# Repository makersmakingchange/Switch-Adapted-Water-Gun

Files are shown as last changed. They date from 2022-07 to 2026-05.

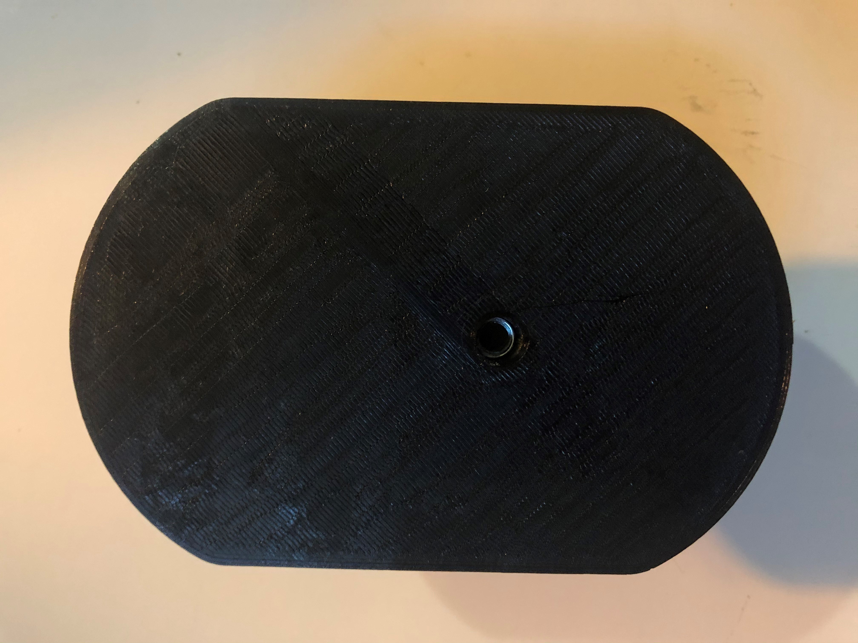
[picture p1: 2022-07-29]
Photos/Step 23.jpg

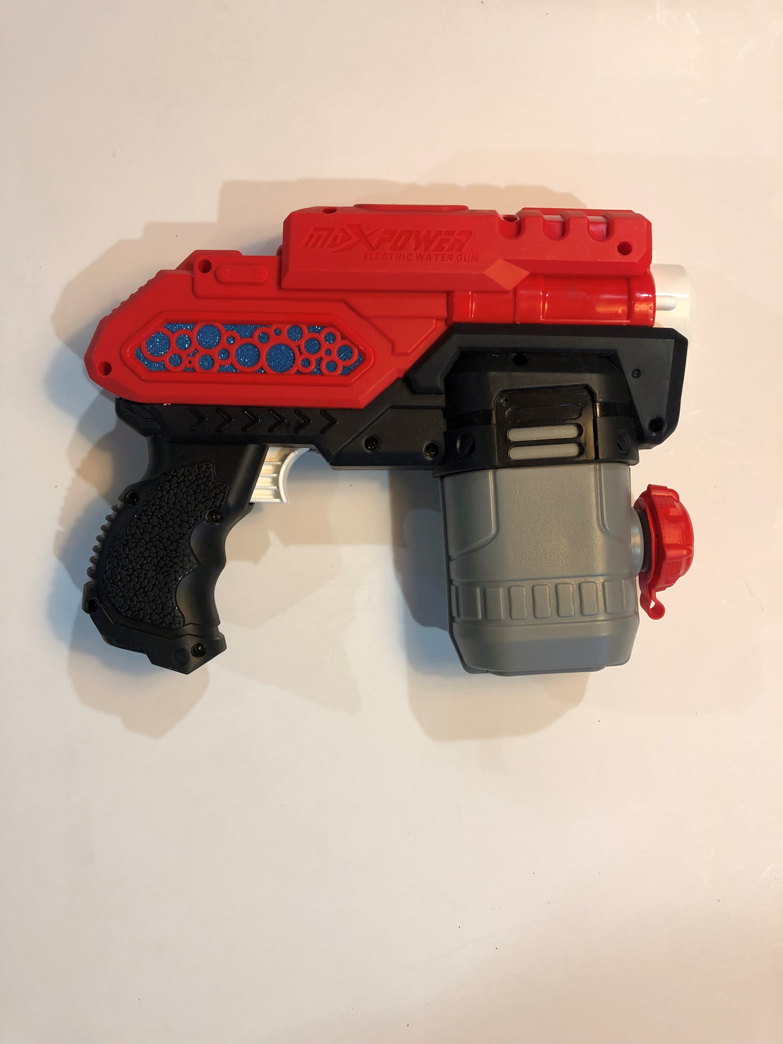
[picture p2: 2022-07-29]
Photos/Step 1.jpg

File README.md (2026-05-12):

# Switch Adapted Water Gun

> [!IMPORTANT]
2026-May-12 Unfortunately, the commercial water gun that this design and adaptation method was based on is no longer available for purchase (https://www.amazon.ca/HITNEXT-Electric-Children-Operated-Automatic/dp/B0919VSGYH). 
>

An adapted water gun that uses a 3.5 mm assistive switch.



## More info at
- [Makers Making Change Project Page](https://makersmakingchange.com/project/switch-adapted-water-gun/)

## Getting Started
#### 1. How to build this device

All of the files and instructions required to adapted the bubble blower are contained within this repository. Refer to the Maker Checklist below.

#### 2. How to request a build of this device

If you would like to obtain a switch adapted bubble blower but do not have the skills or equipment to do so, you may submit a build request through the [MMC Library Page](  https://makersmakingchange.com/project/switch-adapted-water-gun/). The requestor is responsible for the cost of materials and any shipping.

#### 3. How to build this device for someone else

If you have the skills and equipment to build this device, and would like to donate your time to create the switch for someone who needs it, visit the [MMC Maker Wanted](https://makersmakingchange.com/maker-wanted/) section.

## Files
### Documentation
| Document              | Version | Link |
|-----------------------|---------|------|
| Assembly Guide        | 1.0     | [Switch Adapted Water Gun Assembly Guide](/Documentation/Switch_Adapted_Water_Gun_Assembly_Guide_v1.0.pdf)|
| Design Rationale      | 1.0     | [Switch Adapted Water Gun Design Rationale](/Documentation/Switch_Adapted_Water_Gun_Design_Rationale_v1.0.pdf)|
| Bill of Materials     | 1.0     | [Switch Adapted Water Gun Bill of Materials](/Documentation/Working_Documents/Switch_Adapted_Water_Gun_BOM.xlsx)|
| Maker Checklist       | 1.0     | [Switch Adapted Water Gun Maker Checklist](/Documentation/Switch_Adapted_Water_Gun_Maker_Checklist_v1.0.pdf)|
| User Guide            | 1.0     | [Switch Adapted Water Gun User Guide](/Documentation/Switch_Adapted_Water_Gun_User_Guide_v1.0.pdf)|
| Changelog             | 1.0     | [Switch Adapted Water Gun Changelog](/Documentation/Switch_Adapted_Water_Gun_Changelog_v1.0.pdf)|

## Attribution
Toy adaption by Kerilyn Kennedy – Makers Making Change

3D Printed Water Gun Stand designed by Kerilyn Kennedy – Makers Making Change

Documentation by Neil Squire / Makers Making Change

## License
<br /><span xmlns:dct="http://purl.org/dc/terms/" property="dct:title">Switch Adapted Water Gun</span> by <a xmlns:cc="http://creativecommons.org/ns#" href="www.makersmakingchange.com" property="cc:attributionName" rel="cc:attributionURL">Neil Squire</a> is licensed under a <a rel="license" href="http://creativecommons.org/licenses/by-sa/4.0/">Creative Commons Attribution-ShareAlike 4.0 International License</a>.

----

<!-- ABOUT MMC START -->
## About Makers Making Change
[Makers Making Change Logo](https://www.makersmakingchange.com/)

Makers Making Change is a program of [Neil Squire](https://www.neilsquire.ca/), a Canadian non-profit that uses technology, knowledge, and passion to empower people with disabilities.

Makers Making Change leverages the capacity of community based Makers, Disability Professionals and Volunteers to develop and deliver affordable Open Source Assistive Technologies.

 - Website: [www.MakersMakingChange.com](https://www.makersmakingchange.com/)
 - GitHub: [makersmakingchange](https://github.com/makersmakingchange)
 - Bluesky: [@makersmakingchange.bsky.social](https://bsky.app/profile/makersmakingchange.bsky.social)
 - Instagram: [@makersmakingchange](https://www.instagram.com/makersmakingchange)
 - Facebook: [makersmakechange](https://www.facebook.com/makersmakechange)
 - LinkedIn: [Neil Squire Society](https://www.linkedin.com/company/neil-squire-society/)
 - Thingiverse: [makersmakingchange](https://www.thingiverse.com/makersmakingchange/about)
 - Printables: [MakersMakingChange](https://www.printables.com/@MakersMakingChange)

### Contact Us
For technical questions, to get involved, or to share your experience we encourage you to [visit our website](https://www.makersmakingchange.com/) or [contact us](https://www.makersmakingchange.com/s/contact).
<!-- ABOUT MMC END -->

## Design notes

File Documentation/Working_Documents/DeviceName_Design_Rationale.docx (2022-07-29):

# Introduction

We were brought the idea of adding a switch adapted water gun to the MMC library by the IWK. People with limited hand function might not be able to hold a water gun or do the pumping required to operate most water guns. They also might have difficulty pulling the trigger on a water gun as they often require a medium-high activation force. The Switch Adapted Water Gun can be used with just the push of a 3.5mm switch.

# Research

## Commercial Alternatives:

Water Gun with Lights Switch Adapted - $58.10

Switch-adapted Water Gun Soaker (https://www.seemethrive.org/product-page/switch-adapted-water-gun-soaker) - $45.00

## DIY Alternatives:

Adaptions 4 Kidz: Switch Adapted Water Gun Fun (http://adaptions4kidz.blogspot.com/2012/07/switch-adapted-water-gun-fun.html)

# Requirements

## Goals

G01 | Switch adapt the water gun
G02 | Design a 3D printed stand for the water gun
G03

## Functional Requirements

F01 | That the water gun can be adapted to work with a 3.5mm switch.
F02
F03

## Non-functional Requirement

NF01 | That the adaption is easy enough so other volunteer makers can do it themselves.
NF02
NF03

## Constraints

C01
C02
C03

# Ideation

The water gun planned to be used in this project is shown below. It is a battery-operated water gun that requires no pumping to squirt water. It was purchased from Amazon (https://www.amazon.ca/Electric-Battery-Operated-Swimming-Fighting/dp/B08S79325P?rnid=12035759011&s=toys). The idea is to add a jack in parallel with the existing switch in the water gun.

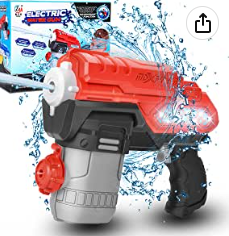
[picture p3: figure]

# Conceptual Design

## Concept 1 – Adding the Assistive Switch in Parallel

The original concept for the water gun adaptation was to be able to add an assistive switch in parallel with the existing switch. This allows for either the original trigger or the assistive switch to work to operate the toy. However, upon further investigation it was determined that it was quite difficult to get access to the original switch. As shown below, a drill was used to cut through the plastic to get access to the switch wires. Once a few holes were drilled, flush cutters were used to snap the reminder of the plastic away. Even with this new opening, I was still not able to access the original switch to solder in parallel. If one wanted the switch in parallel, it could be done by cutting into the yellow and blue wires and soldering in the assistive switch. Note, there is not much room to work with as wires a small and there is not much slack to work with. It can be done but it is not recommended to do it this way for a group build as it was time consuming to drill into this piece and there is a risk of damaging the wires when drilling through.

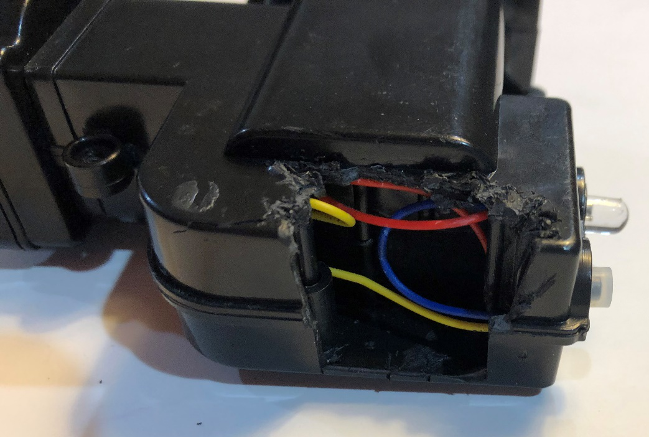
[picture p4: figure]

## Concept 2 – Adding the Assistive Switch in Series

The next route taken was to add the assistive switch in series with the original switch. This means that the original switch would have to be held in the “on” position all the time in order for the assistive switch to work. This would most easily be done with a battery interrupter.

# Detailed Design

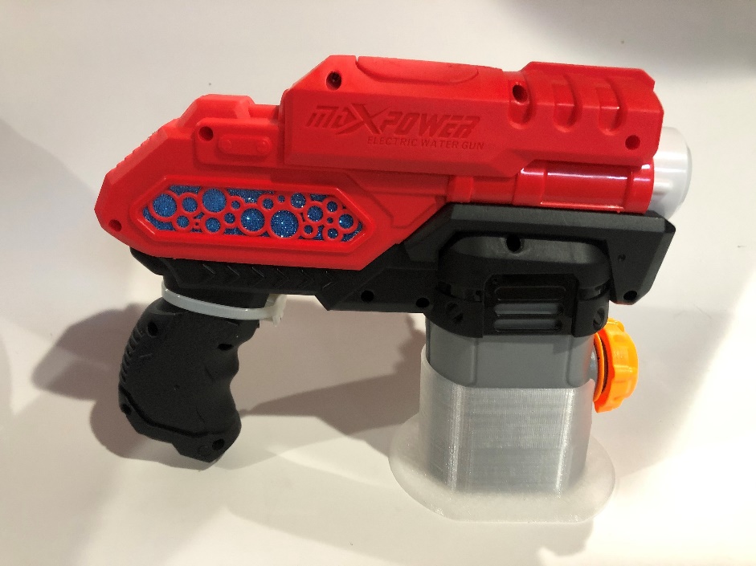
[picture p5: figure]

This is the switch adapted water gun. It was adapted using a battery interrupter. As shown above, a zip tie is used to hold the trigger in the “on” position at all times. This is required to operate the assistive switch because the switch is in series.

# Testing

The water gun was testing by plugging in a 3.5mm switch.

# Opportunities for Improvement

- Find an easier way to cut into the battery compartment so that the switch could be more easily put in parallel rather than in series to eliminate the need for a battery interrupter.

© 2022 by Kerilyn Kennedy – Makers Making Change This work is licensed under the CC BY SA 4.0 License: http://creativecommons.org/licenses/by-sa/4.0 Files available at https://makersmakingchange.com/project/switch-adapted-water-gun/ Page 1 of 1

V1.0 | JUNE 2022 Switch Adapted Water Gun Design Rationale

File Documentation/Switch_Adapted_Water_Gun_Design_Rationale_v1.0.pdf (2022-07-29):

V1.0 | JUNE 2022

## Switch Adapted Water Gun

## DESIGN RATIONALE

© 2022 by Kerilyn Kennedy – Makers Making Change This work is licensed under the CC BY SA 4.0 License: http://creativecommons.org/licenses/by-sa/4.0 Files available at https://makersmakingchange.com/project/switch-adapted-water-gun/ (https://makersmakingchange.com/?post_type=project&p=15490&preview=true)

### Introduction

We were brought the idea of adding a switch adapted water gun to the MMC library by the IWK. People with limited hand function might not be able to hold a water gun or do the pumping required to operate most water guns. They also might have difficulty pulling the trigger on a water gun as they often require a medium-high activation force. The Switch Adapted Water Gun can be used with just the push of a 3.5mm switch.

### Research

### Commercial Alternatives:

Water Gun with Lights Switch Adapted - $58.10

Switch-adapted Water Gun Soaker (https://www.seemethrive.org/product-page/switch-adapted-water-gun-soaker) - $45.00

### DIY Alternatives:

Adaptions 4 Kidz: Switch Adapted Water Gun Fun (http://adaptions4kidz.blogspot.com/2012/07/switch-adapted-water-gun-fun.html)

### Requirements

### Goals

G01 | Switch adapt the water gun
G02 | Design a 3D printed stand for the water gun
G03

### Functional Requirements

F01 | That the water gun can be adapted to work with a 3.5mm switch.
F02
F03

### Non-functional Requirement

NF01 | That the adaption is easy enough so other volunteer makers can do it themselves.
NF02
NF03

## DESIGN RATIONALE

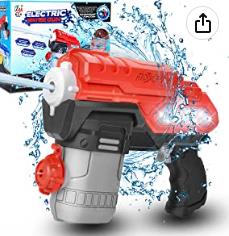
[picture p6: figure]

© 2022 by Kerilyn Kennedy – Makers Making Change

### Constraints

C01
C02
C03

### Ideation

The water gun planned to be used in this project is shown below. It is a battery-operated water gun that requires no pumping to squirt water. It was purchased from Amazon. (https://www.amazon.ca/Electric-Battery-Operated-Swimming-Fighting/dp/B08S79325P?rnid=12035759011&s=toys) The idea is to add a jack in parallel with the existing switch in the water gun.

### Conceptual Design

### Concept 1 – Adding the Assistive Switch in Parallel

The original concept for the water gun adaptation was to be able to add an assistive switch in parallel with the existing switch. This allows for either the original trigger or the assistive switch to work to operate the toy. However, upon further investigation it was determined that it was quite difficult to get access to the original switch. As shown below, a drill was used to cut through the plastic to get access to the switch wires. Once a few holes were drilled, flush cutters were used to snap the reminder of the plastic away. Even with this new opening, I was still not able to access the original switch to solder in parallel. If one wanted the switch in parallel, it could be done by cutting into the yellow and blue wires and soldering in the assistive switch. Note, there is not much room to work with as wires a small and there is not much slack to work with. It can be done but it is not recommended to do it this way for a group build as it was time consuming to drill into this piece and there is a risk of damaging the wires when drilling through.

## DESIGN RATIONALE

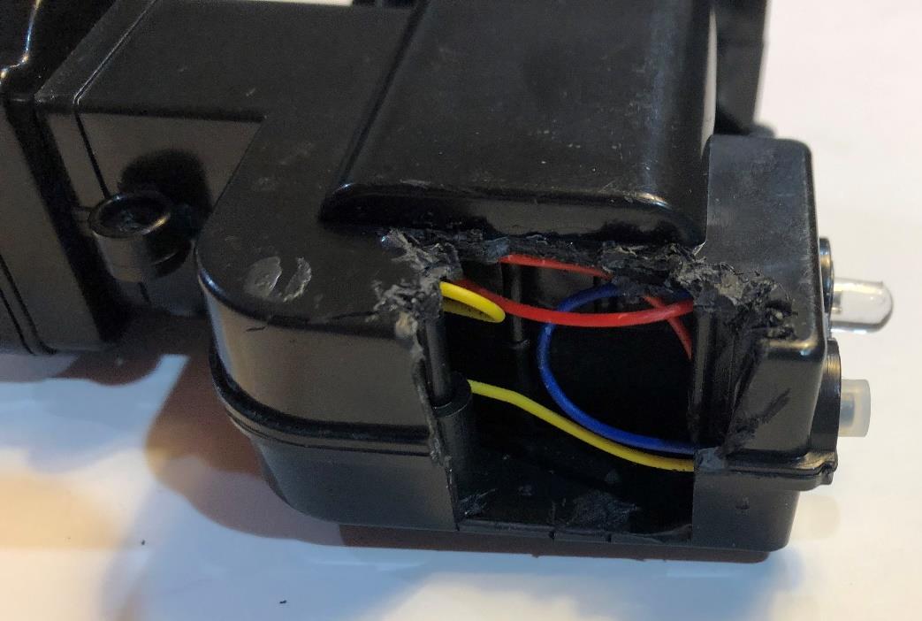
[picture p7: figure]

© 2022 by Kerilyn Kennedy – Makers Making Change

### Concept 2 – Adding the Assistive Switch in Series

The next route taken was to add the assistive switch in series with the original switch. This means that the original switch would have to be held in the “on” position all the time in order for the assistive switch to work. This would most easily be done with a battery interrupter.

## DESIGN RATIONALE

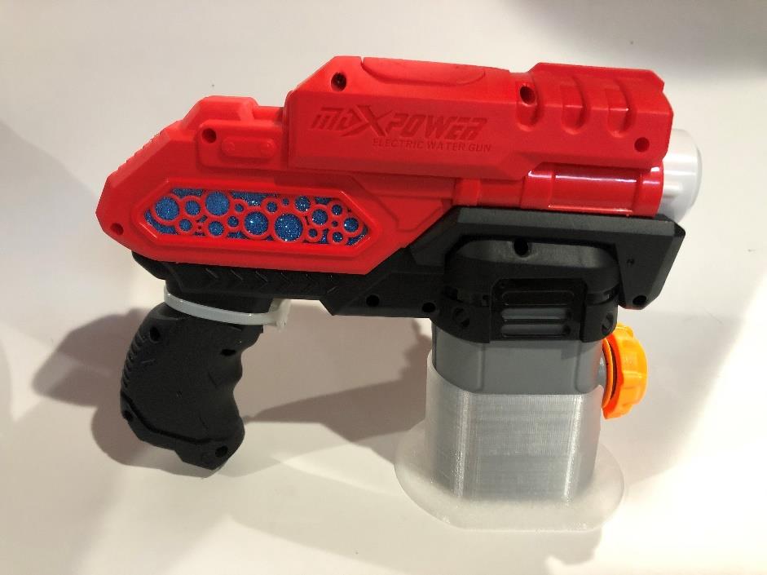
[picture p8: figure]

© 2022 by Kerilyn Kennedy – Makers Making Change

### Detailed Design

This is the switch adapted water gun. It was adapted using a battery interrupter. As shown above, a zip tie is used to hold the trigger in the “on” position at all times. This is required to operate the assistive switch because the switch is in series.

### Testing

The water gun was testing by plugging in a 3.5mm switch.

### Opportunities for Improvement

- Find an easier way to cut into the battery compartment so that the switch could be more easily put in parallel rather than in series to eliminate the need for a battery interrupter.

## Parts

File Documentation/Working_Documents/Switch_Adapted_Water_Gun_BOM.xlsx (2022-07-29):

Device: Switch Adapted Water Gun |  | Total Cost | Total Print time (hr) | Total filament (g)
Version: V1.0 | Date Created: JUNE 2022 | $30.93 | 3.25 | 66
Commercial Parts:
Part type (Electrical. Mechanical, Sanitization, ect) | Part Name | Quantity Needed | Pkg Quantity | Price per package | Price per Unit | Price for qty needed | Link
Electric Water Gun | ‎B0B2W74QBN | 1 | 1 | $22.45 | $22.45 | $22.45 | HITNEXT Electric Water Gun, Automatic Squirt Guns Battery Operated Water Blaster Gun 300CC Long Range Shooting Water Toy Gifts for Kids 3+ Yard Beach Outdoor Games Water Fighting : Amazon.ca: Everything Else (https://www.amazon.ca/HITNEXT-Electric-Children-Operated-Automatic/dp/B0919VSGYH)
3.5mm mono jack | CP-3502MJ-ND | 1 | 1 | $2.14 | $2.14 | $2.14 | https://www.digikey.ca/short/pq1d1z
Copper Foil Tape | VGEBYdxt37285gi-01 | 1 | 100 | $9.50 | $0.10 | $0.10 | Home Mart Banding cables Cable ties Self-locking electric wire cables Zip ties 2.2 mm x 80 mm 100 pieces, Cable Ties - Amazon Canada (https://www.amazon.ca/Home-Mart-Banding-Self-locking-electric/dp/B074RYXBSX?rnid=12035759011)
AA Batteries |  | 4 | 4 | $3.98 | $0.99 | $3.98 | https://www.walmart.ca/en/ip/energizer-max-aa-batteries-4-pack-double-a-alkaline-batteries/PRD6FBLLXWUHPD1
Zip Tie | ‎S-77 | 1 | 100 | $1.69 | $0.02 | $0.02 | https://www.amazon.ca/Home-Mart-Banding-Self-locking-electric/dp/B074RYXBSX?rnid=12035759011
1/4″-20 UNC Hex Bolt, 1/2″ Length |  | 1 | 100 | $10.03 | 0.1003 | $0.10 | www.mcmaster.com/92865a537
1/4″-20 UNC Tee Nut Insert |  | 1 | 100 | $16.30 | $0.16 | $0.16 | https://www.mcmaster.com/90975A025/
3D Printed Parts ESTIMATED PRICING USING 1KG ROLL COST: | $30.00
Part | Description | Quantity Needed | TOTAL Mass (g) | Estimated Price | Print Time (Min) | Link
Water Gun Stand |  | 1 | 66 | $1.98 | 195
 |  |  |  | $0.00
 |  |  |  | $0.00
 |  |  |  | $0.00
 |  |  |  | $0.00
 |  |  | Total Print Cost: | $1.98
Tools for Assembly
Alternatives (if there are other sources for some parts link them below)
Part and description | Link
There are other links for the water gun found on amazon | Electric Water Gun, Battery Operated Squirt Guns with Cool LED Lights, 300CC Long Range Water Blaster for Kids Adults Swimming Pool Beach Party Water Fighting (Black), Water Guns, Blasters & Soakers - Amazon Canada (https://www.amazon.ca/Electric-Battery-Operated-Swimming-Fighting/dp/B08S79325P?rnid=12035759011&s=toys)
Zip Ties can be found at your local dollar store, walmart, canadian tire, etc.

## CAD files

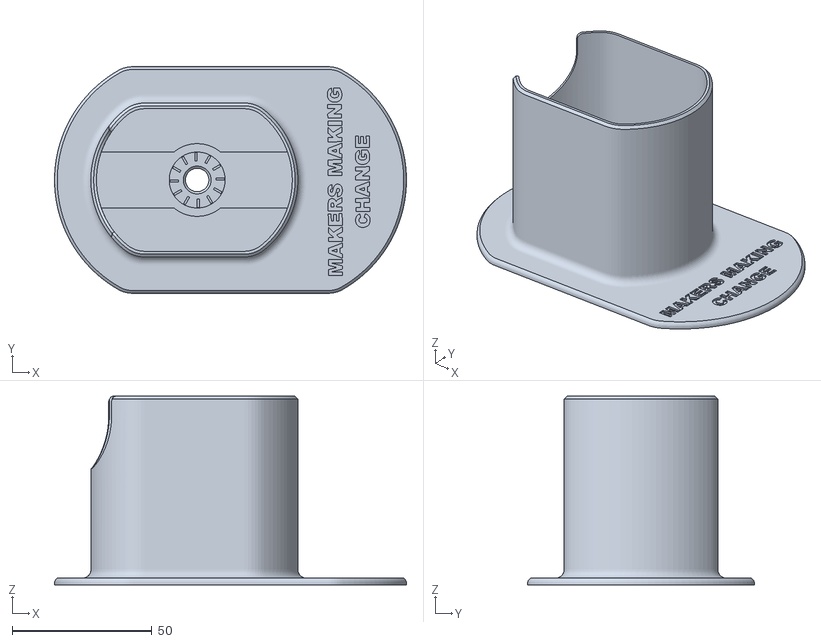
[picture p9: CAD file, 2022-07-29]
Build_Files/3D_Print_Files/Water_Gun_Stand.stl
125.8 x 81.0 x 67.4

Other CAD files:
Design_Files/Water_Gun_Stand.f3z

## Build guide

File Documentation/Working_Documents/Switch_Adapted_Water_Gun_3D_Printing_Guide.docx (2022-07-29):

# 3D Printing Summary

Metrics | Water Gun Stand
Total Print Time (min) | 193
Total Number of Components | 1
Typical Total Mass (g) | 66
Typical Number of Print Setups | 1

# 3D Printing Settings

Print File Name | Qty | Total Print Time (hr:min) | Mass (g) | Infill (%) | Support (Y/N) | Layer Height/ Nozzle Diameter (mm) | Notes (orientation, special settings, etc.)
Water_Gun_Stand.stl | 1 | 3:13 | 66 | 20 | N | 0.3/0.4 | Print in orientation given in STL

# Post-Processing

This device is printed without supports; hence no post processing is required.

# Customization Options

The user can request the colour of the stand or any other custom markings they may want on the device.

# Examples of Quality Prints

Below are pictures of what the quality of the print is expected to look like.

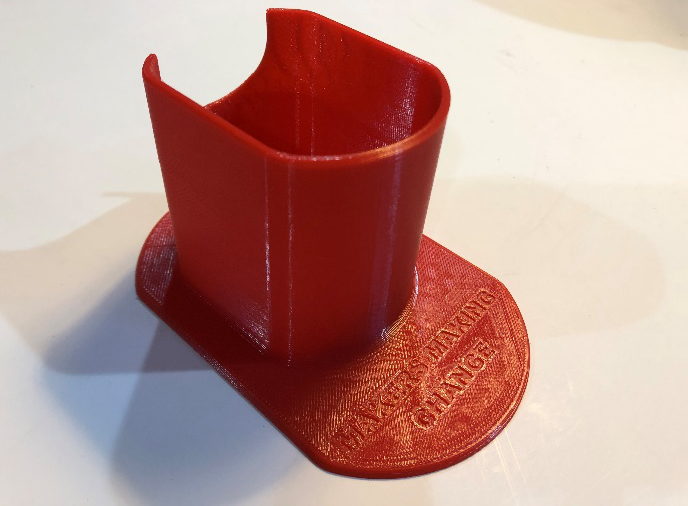
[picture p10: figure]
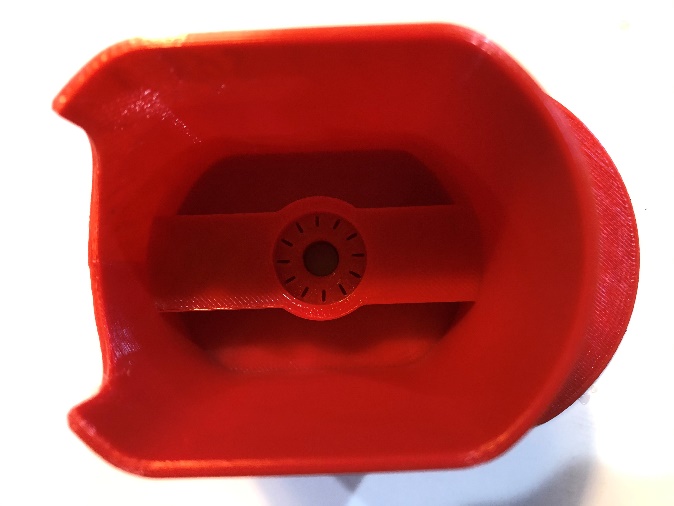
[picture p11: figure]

© 2022 by Kerilyn Kennedy – Makers Making Change This work is licensed under the CC BY SA 4.0 License: http://creativecommons.org/licenses/by-sa/4.0 Files available at https://makersmakingchange.com/project/switch-adapted-water-gun/ Page 1 of 2

V1.0 | JUNE 2022 Switch Adapted Water Gun 3D Printing Guide

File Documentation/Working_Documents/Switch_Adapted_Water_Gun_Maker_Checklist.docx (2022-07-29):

# Maker To Do List

- Read through the Assembly Guide to become familiar with required components, tools, supplies, and safety gear and overall assembly steps.
- Ask the User if they already own a 3.5mm switch – if they don’t, let them know that they can request one from the MMC library.
- Talk to the User about customization options (e.g., color, any special requests, etc.)
- Order hardware components.
- Gather tools, supplies, and safety equipment.
- Adapt the Water Gun.
- Print and assemble 3D Printed Water Gun Stand.
- Test device.
- Print “User Quick Guide.”

# Items to Give to User

- Adapted Water Gun.
- “User Quick Guide.”

© 2022 by Kerilyn Kennedy – Makers Making Change This work is licensed under the CC BY SA 4.0 License: http://creativecommons.org/licenses/by-sa/4.0 Files available at <Replace with MMC Library Link> Page 1 of 1

V1.0 | JUNE 2022 Switch Adapted Water Gun Maker Checklist

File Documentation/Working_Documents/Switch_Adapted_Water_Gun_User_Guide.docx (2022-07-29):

## Introduction

This is a switch adapted water gun that is compatible with 3.5mm switches. This device may be beneficial to someone with limited hand function that is interested in using a water gun.

Battery compartment

## Features

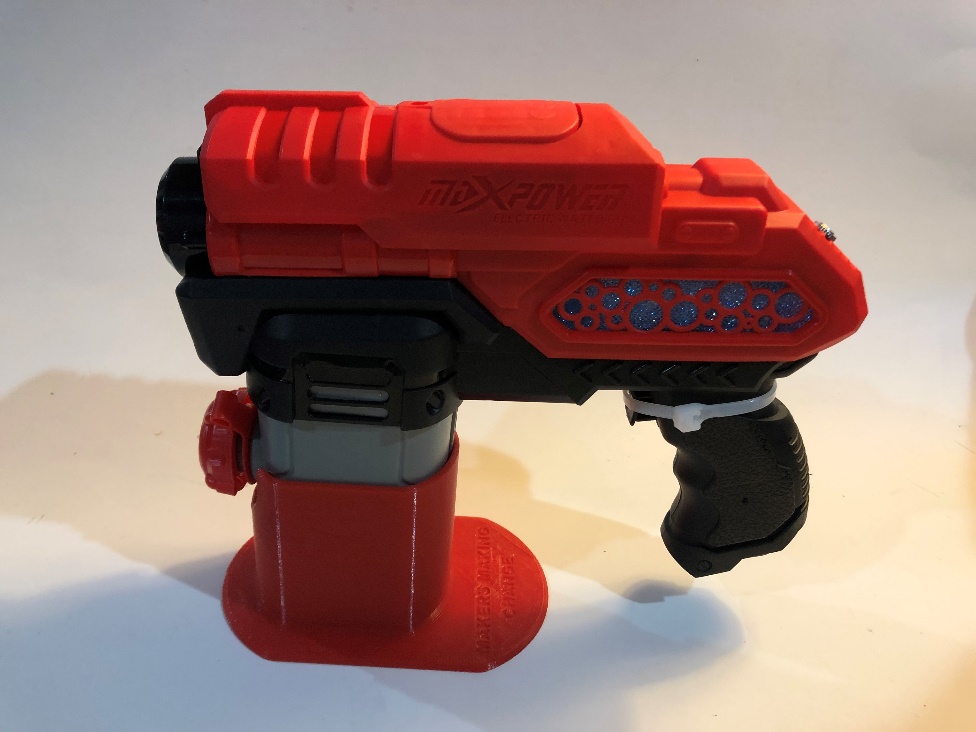
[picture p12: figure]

3.5mm jack

Nozzle

3D Printed Water Gun Stand

Water compartment

## Usage

The Switch Adapted Water Gun can be used by first filling it up with water. Next, plug in a 3.5mm switch into the back of the water gun. Once the switch is pressed, the water gun is activated.

## Compatibility

The Switch Adapted Water Gun should be compatible with any 3.5mm switch.

## Specifications

Length (mm) | Width (mm) | Height (mm) | Mass (g)
215 | 165 | 60 | 272

*The mass given is the mass of the empty water gun.

## Cleaning

The device can be wiped down with a damp cloth. When not in use, empty out the water compartment in the gun.

## Changing the Batteries

The batteries can be accessed by removing the screw from the battery compartment located on the top of the water gun. The device takes 4 AA batteries. This water gun was adapted using a battery interrupter. If the batteries need to be changed in the device, the battery interrupter will have to be wedged between one of the batteries and the battery spring in the location shown below. The battery interrupter shown below is centered on the battery to ensure it is touching both the battery and the spring located on the lid. If the device is still not working once you’ve changed the batteries, this is likely caused by the battery interrupter not being placed correctly. If the water gun stays in the “on position” even though you are not holding down a switch, this means the battery interrupter is not doing its job and means it needs to be adjusted.

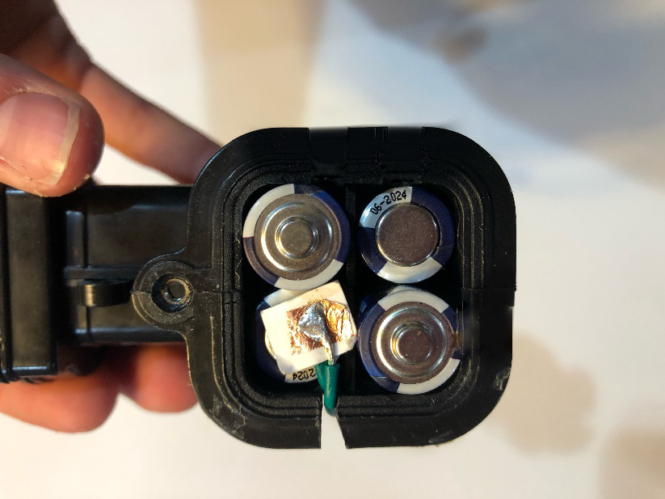
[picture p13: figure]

© 2022 by Kerilyn Kennedy – Makers Making Change This work is licensed under the CC BY SA 4.0 License: http://creativecommons.org/licenses/by-sa/4.0 Files available at https://makersmakingchange.com/project/switch-adapted-water-gun/ Page 2 of 3

V1.0 | JUNE 2022 Switch Adapted Water Gun user Quick Guide

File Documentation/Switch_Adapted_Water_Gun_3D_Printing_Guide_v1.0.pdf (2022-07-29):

V1.0 | JUNE 2022

## Switch Adapted Water Gun

## 3D PRINTING GUIDE

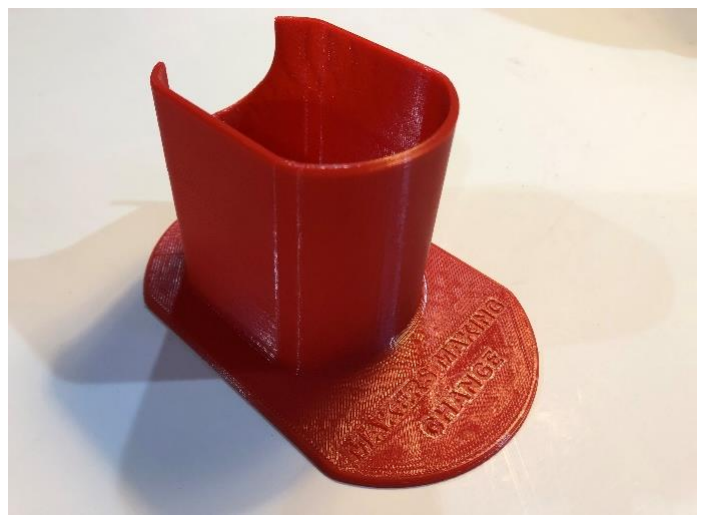
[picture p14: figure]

© 2022 by Kerilyn Kennedy – Makers Making Change

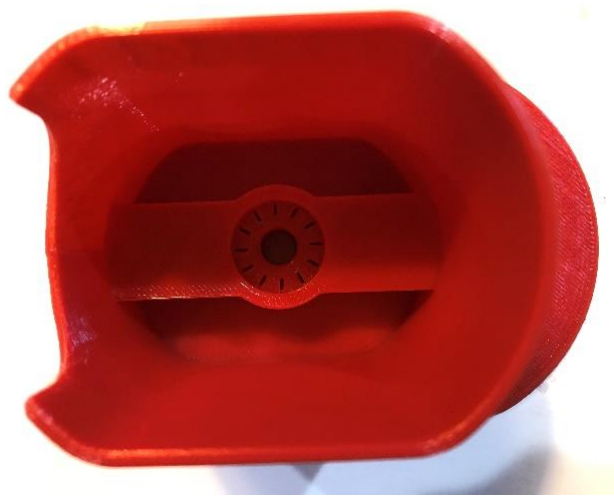
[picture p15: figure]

This work is licensed under the CC BY SA 4.0 License: http://creativecommons.org/licenses/by-sa/4.0 Files available at https://makersmakingchange.com/project/switch-adapted-water-gun/ (https://makersmakingchange.com/?post_type=project&p=15490&preview=true)

### 3D Printing Summary

Metrics | Water Gun Stand
Total Print Time (min) | 193
Total Number of Components | 1
Typical Total Mass (g) | 66
Typical Number of Print Setups | 1

### 3D Printing Settings

Print File Name | Qty | Total Print Time (hr:min) | Mass (g) | Infill (%) | Support (Y/N) | Layer Height/ Nozzle Diameter (mm) | Notes (orientation, special settings, etc.)
Water_Gun_Stand. stl | 1 | 3:13 | 66 | 20 | N | 0.3/0.4 | Print in orientation given in STL

### Post-Processing

This device is printed without supports; hence no post processing is required.

### Customization Options

The user can request the colour of the stand or any other custom markings they may want on the device.

### Examples of Quality Prints

Below are pictures of what the quality of the print is expected to look like.

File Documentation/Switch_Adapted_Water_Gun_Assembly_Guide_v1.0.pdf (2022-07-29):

V1.0 | JUNE 2022

# Switch Adapted Water Gun

# ASSEMBLY GUIDE

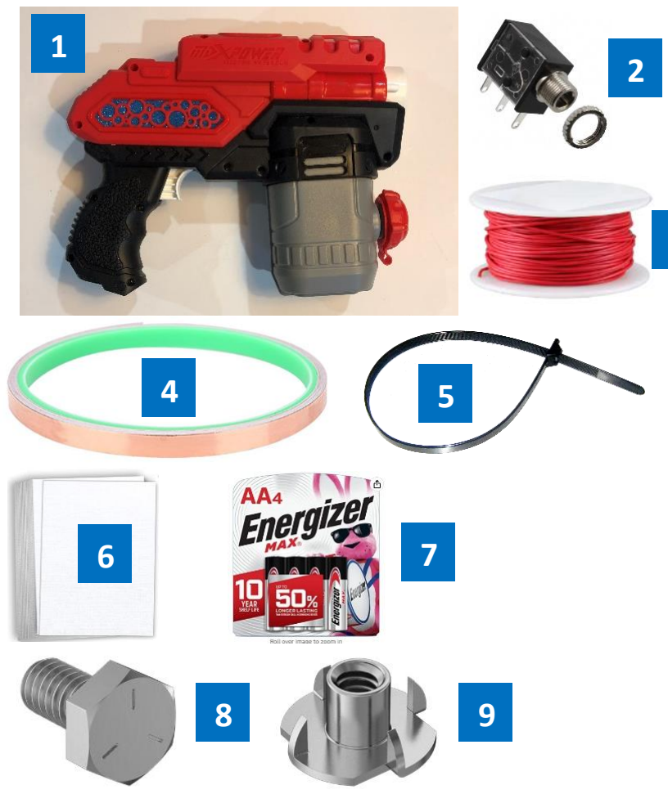
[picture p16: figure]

© 2022 by Kerilyn Kennedy – Makers Making Change This work is licensed under the CC BY SA 4.0 License: http://creativecommons.org/licenses/by-sa/4.0
Files available at | https://makersmakingchange.com/project/switch-adapted-water-gun/ (https://makersmakingchange.com/?post_type=project&p=15490&preview=true) | Page 1 of 13

# Required Components

## BOM

## 1. Electric Water Gun 2. 3.5mm mono jack and nut 3. 2 pieces of wire 15cm long 4. Copper Tape 8mm long 5. Zip tie 6. 1cm x 1cm card stock or paper 7. 4 AA batteries 8. 1/4″-20 UNC Hex Bolt, 1/2″ Length 9. 1/4″-20 UNC Tee Nut Insert

# Required Tools

## - Drill with ¼” bit - Small flat head or Phillips screwdriver (it must be skinny as the screws are in deep) - Flush Cutters - Wire Strippers - Soldering Iron and Solder - Scissors

# Required Personal Protective Equipment (PPE)

## - Safety Glasses

3

# ASSEMBLY GUIDE

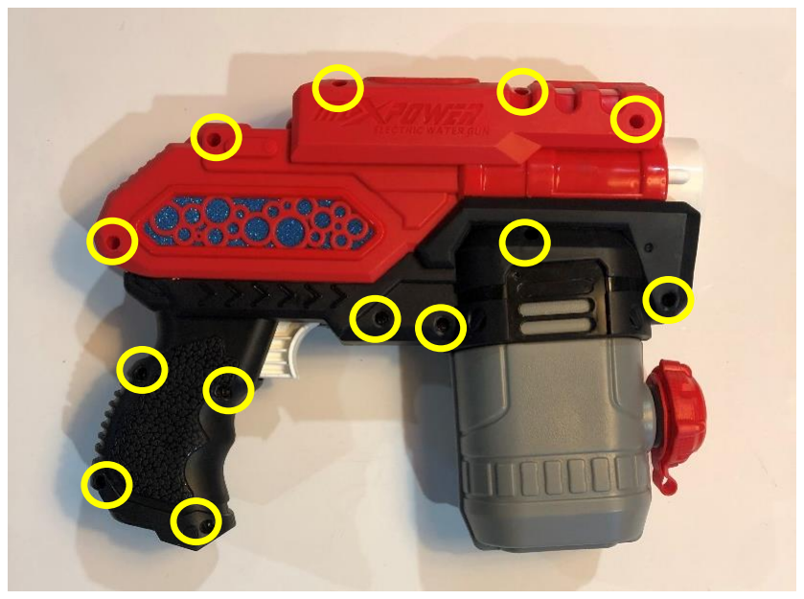
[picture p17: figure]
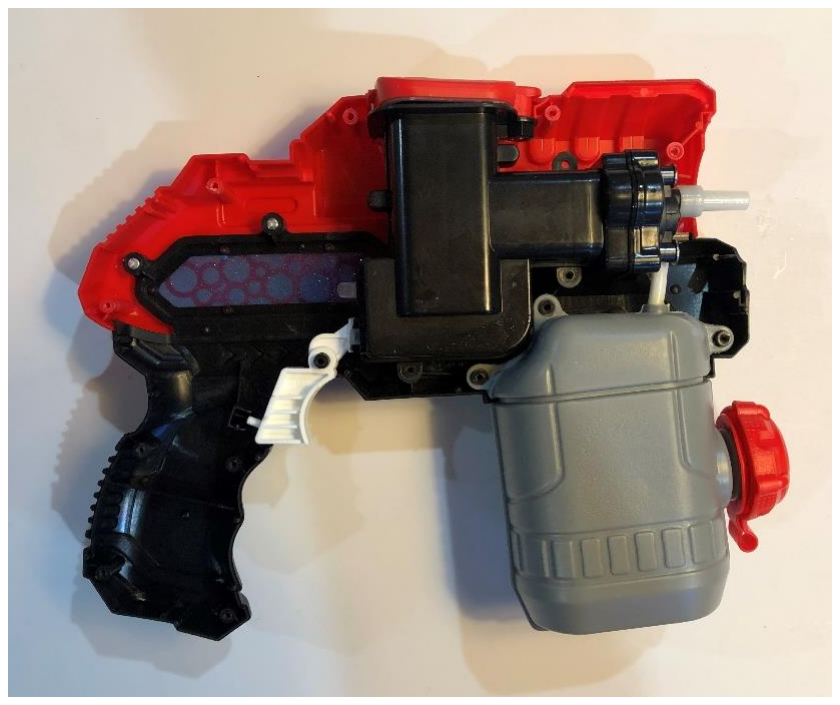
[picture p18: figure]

Files available at | https://makersmakingchange.com/project/switch-adapted-water-gun/ (https://makersmakingchange.com/?post_type=project&p=15490&preview=true) | Page 2 of 13

# Assembly Instructions

## Step 1

Remove 13 screws from the side of the water gun as pictured.

## Step 2

Remove and set aside the half of the water gun that was held down by the screws.

# ASSEMBLY GUIDE

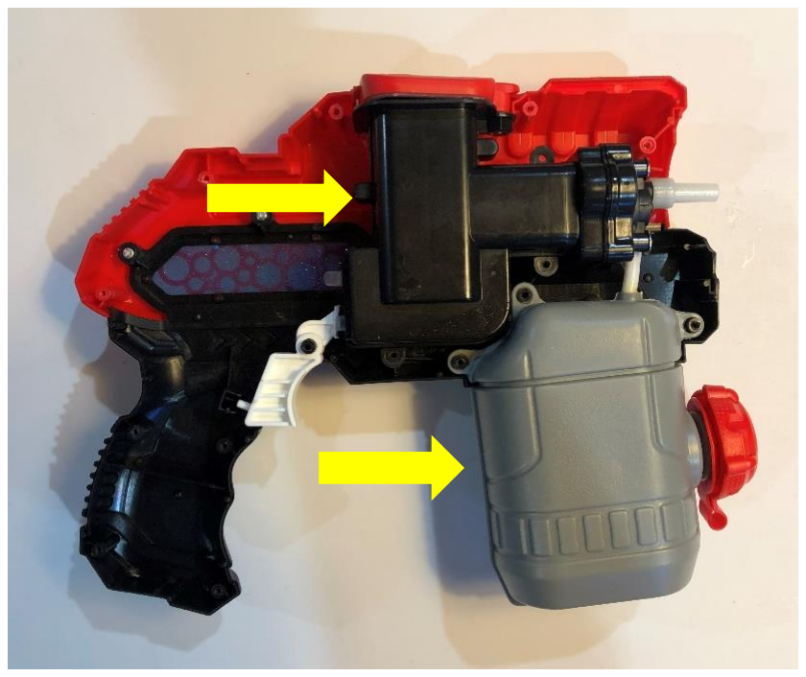
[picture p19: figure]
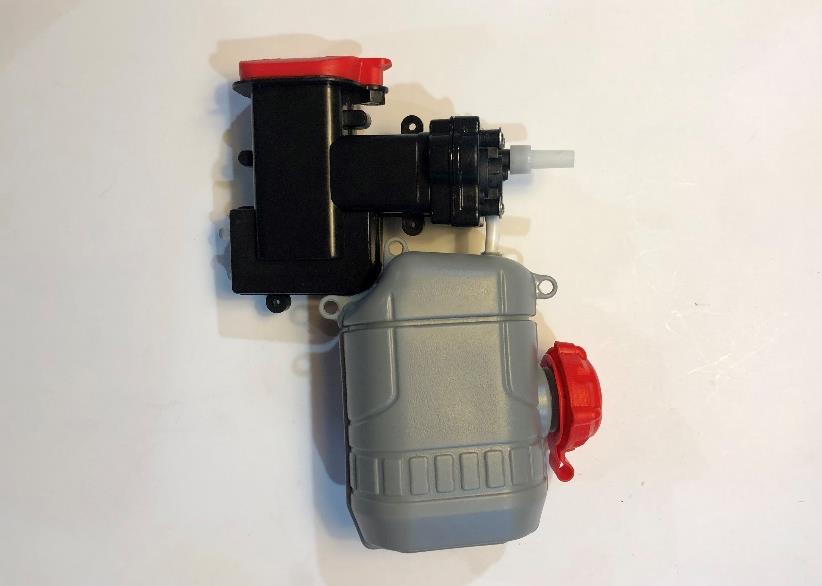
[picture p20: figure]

Files available at | https://makersmakingchange.com/project/switch-adapted-water-gun/ (https://makersmakingchange.com/?post_type=project&p=15490&preview=true) | Page 3 of 13

## Step 3

## Remove any other screws that are holding down the black battery compartment or the grey

water compartment. (Some seemed to have screws others did not).

## Step 4

Remove the battery compartment and the water compartment from the water gun.

# ASSEMBLY GUIDE

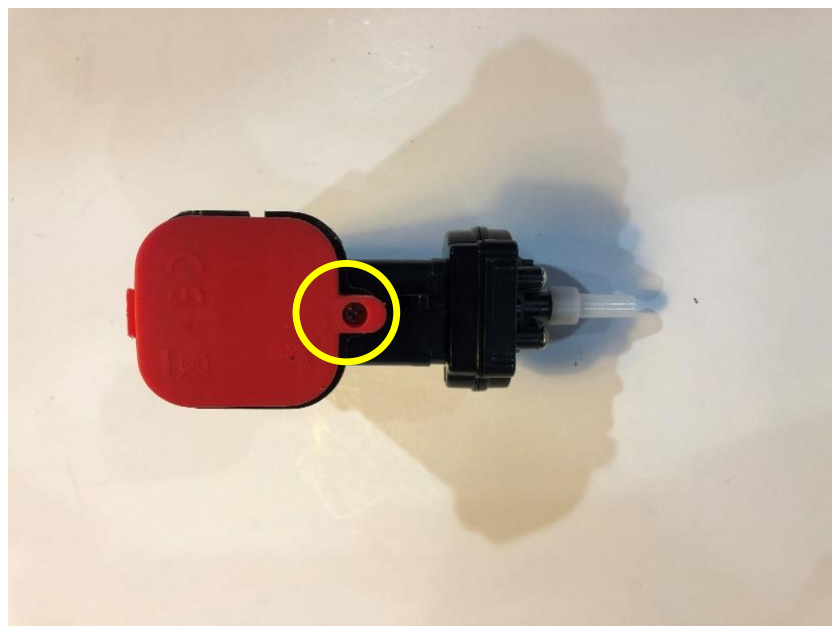
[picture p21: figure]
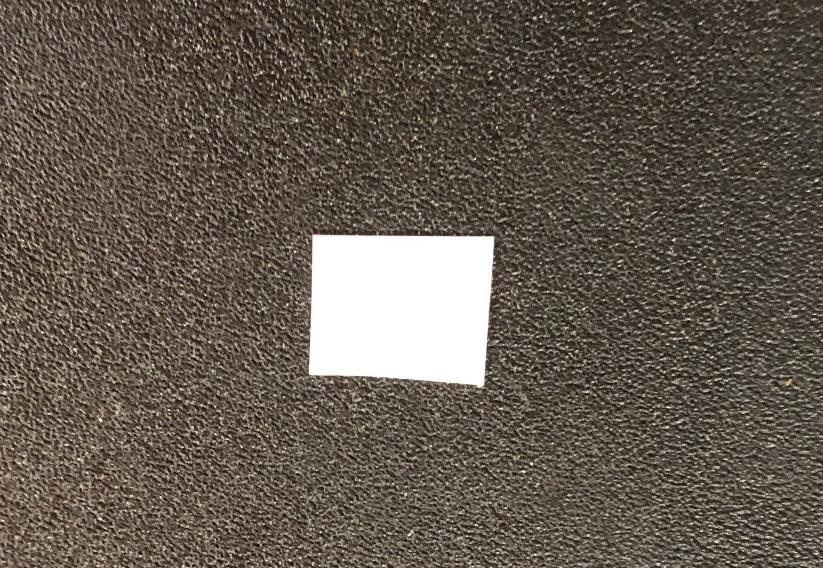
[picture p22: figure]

Files available at | https://makersmakingchange.com/project/switch-adapted-water-gun/ (https://makersmakingchange.com/?post_type=project&p=15490&preview=true) | Page 4 of 13

## Step 5

Remove screw from the top of the battery compartment.

## Step 6

## Using cardstock or paper, cut a small rectangle approximately 1cm x 1cm

# ASSEMBLY GUIDE

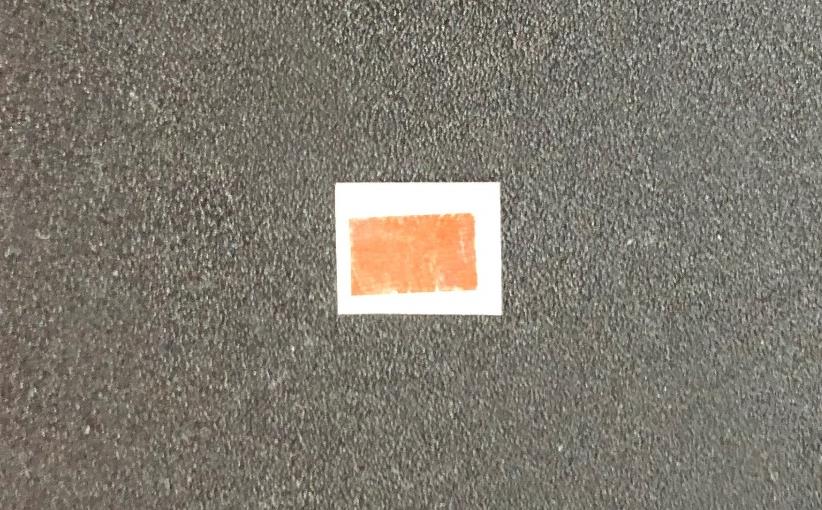
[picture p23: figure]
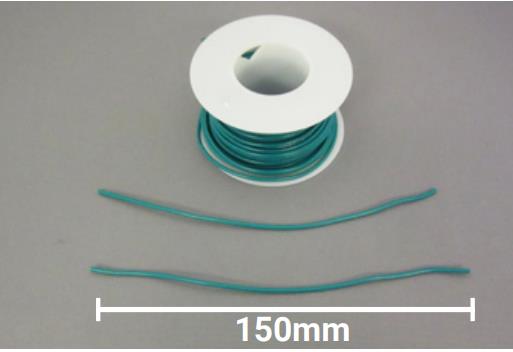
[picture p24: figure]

Files available at | https://makersmakingchange.com/project/switch-adapted-water-gun/ (https://makersmakingchange.com/?post_type=project&p=15490&preview=true) | Page 5 of 13

## Step 7

Cut 2 pieces of copper tape 8mm long (just shorter than the cardstock). Adhere the copper tape on both sides of the cardstock in the centre.

## Step 8

Cut 2 pieces of wire 15cm long.

# ASSEMBLY GUIDE

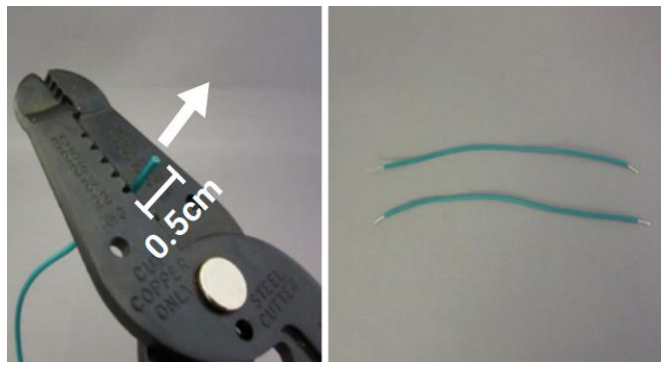
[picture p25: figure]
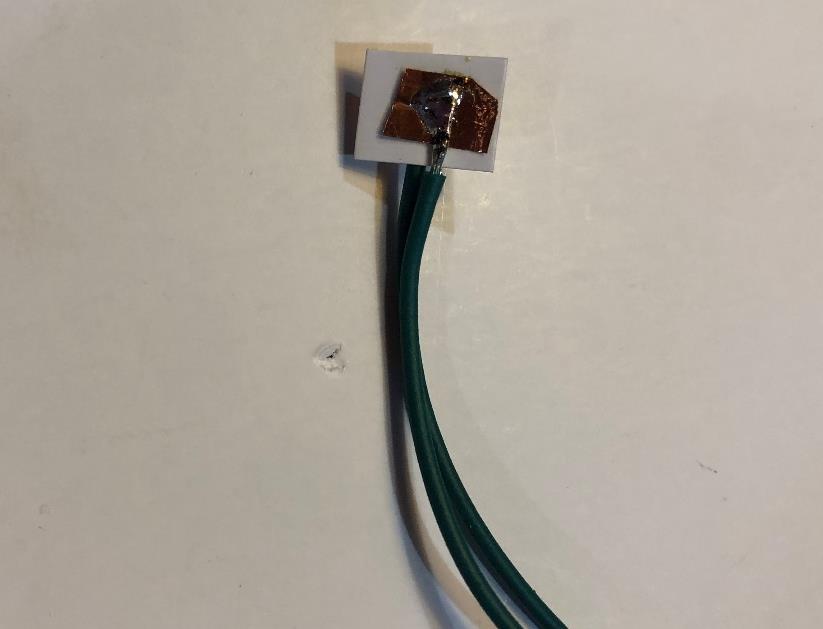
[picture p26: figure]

Files available at | https://makersmakingchange.com/project/switch-adapted-water-gun/ (https://makersmakingchange.com/?post_type=project&p=15490&preview=true) | Page 6 of 13

## Step 9

Strip 0.5cm off both ends of the two wires.

## Step 10

Solder one wire to one side of the copper tape and the second wire to the second side of the copper tape.

# ASSEMBLY GUIDE

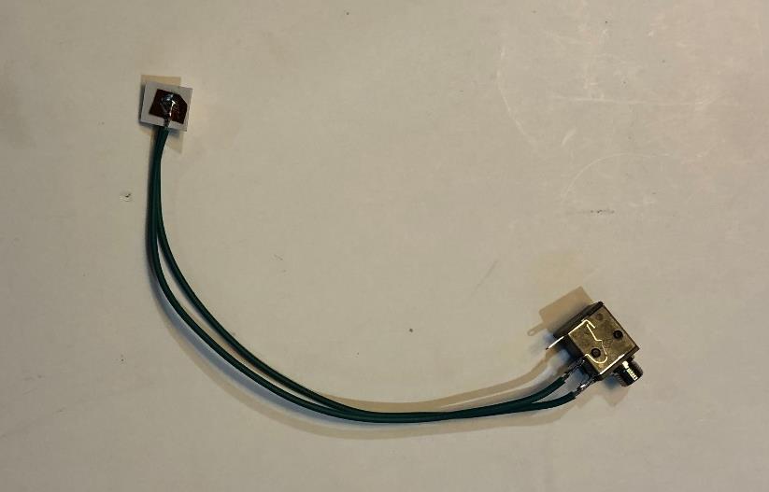
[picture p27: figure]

Files available at | https://makersmakingchange.com/project/switch-adapted-water-gun/ (https://makersmakingchange.com/?post_type=project&p=15490&preview=true) | Page 7 of 13

## Step 11

Solder the other ends of the wires to the two mono jack legs closest to the nut or jack. This device is called a battery interrupter. It will later be placed in between the batteries of the device to allow for the assistive switch to be used instead of the trigger.

## Step 12

Using flush cutters, cut a small slot out of the battery compartment in the position shown below. The slot should be big enough to fit 2 wires out of.

# ASSEMBLY GUIDE

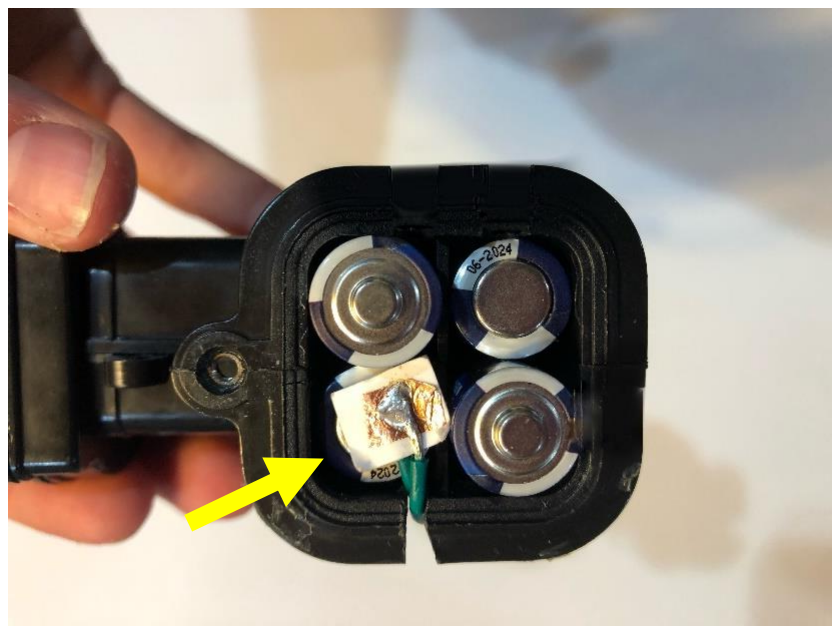
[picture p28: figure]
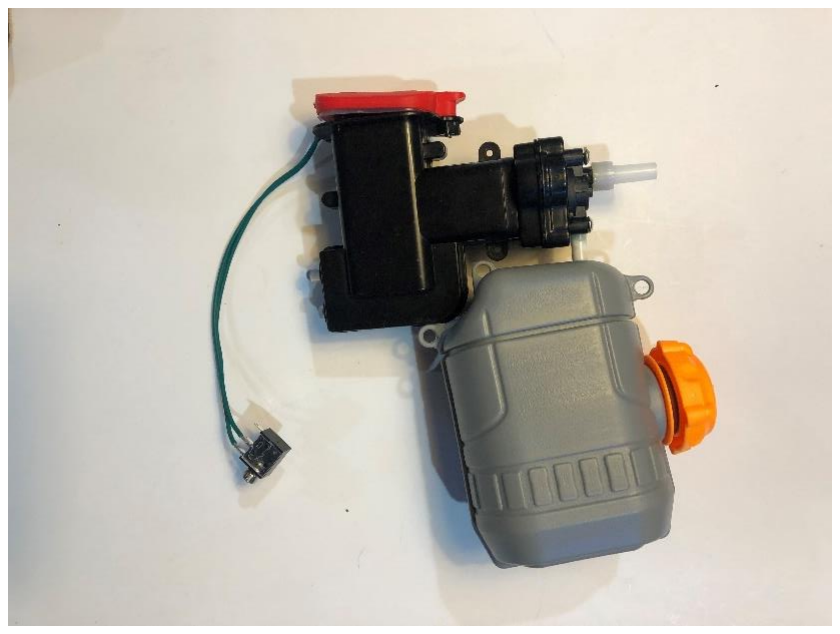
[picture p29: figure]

Files available at | https://makersmakingchange.com/project/switch-adapted-water-gun/ (https://makersmakingchange.com/?post_type=project&p=15490&preview=true) | Page 8 of 13

## Step 13

Insert 4x AA batteries into the battery compartment. Once done, insert the battery interrupter on top of the battery shown below. (It works best on this battery because it gets held down better as it is on the side closest to the battery cover screw. Also, the interrupter has a much easier time reaching the “spring” side of the battery cover which is why this battery position

## was chosen.)

## Step 14

Screw the battery cover back on the battery compartment. Make sure the wires fall in the slot cut in Step 12 so they don’t interfere with the cover.

# ASSEMBLY GUIDE

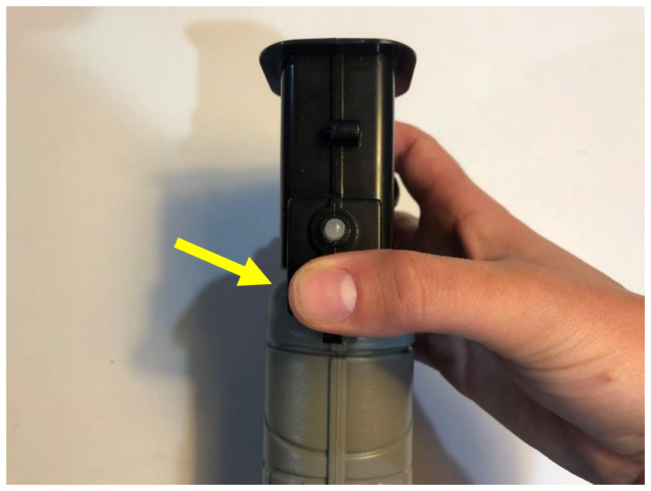
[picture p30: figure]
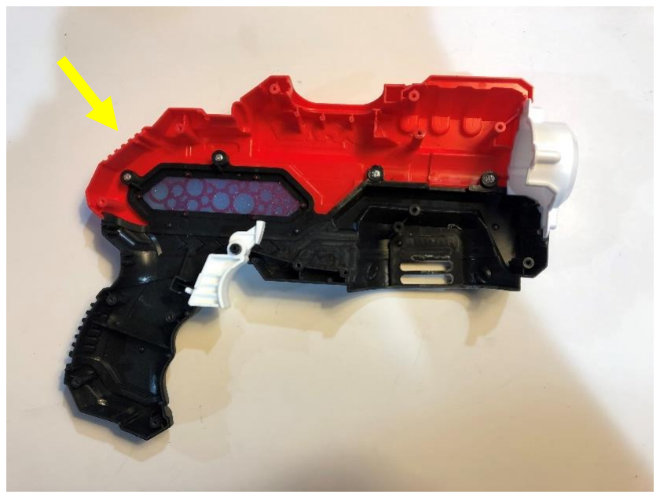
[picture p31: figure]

Files available at | https://makersmakingchange.com/project/switch-adapted-water-gun/ (https://makersmakingchange.com/?post_type=project&p=15490&preview=true) | Page 9 of 13

## Step 15

Test the device. This will be done by plugging in an assistive switch into the jack. The switch on the water gun will have to be held in simultaneously when the switch is activated. If the water gun isn’t working, the battery interrupter likely moved out of place.

## Step 16

Locate this half of the water gun. Drill a 1/4" hole in the gun in the location shown below. Make sure there is enough room for a mono jack to be placed wherever the hole is drilled.

# ASSEMBLY GUIDE

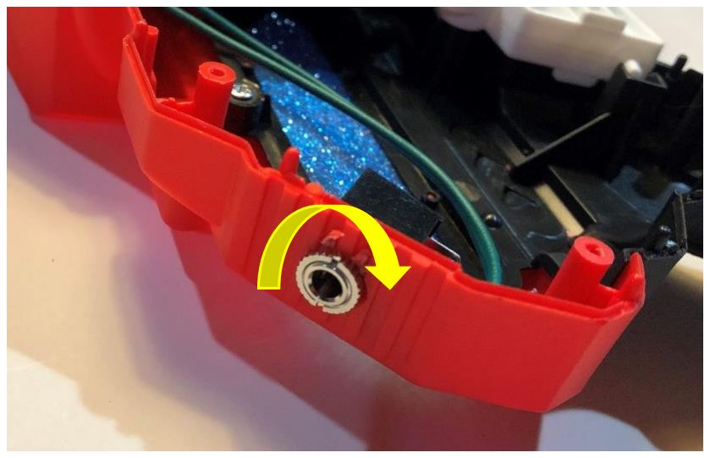
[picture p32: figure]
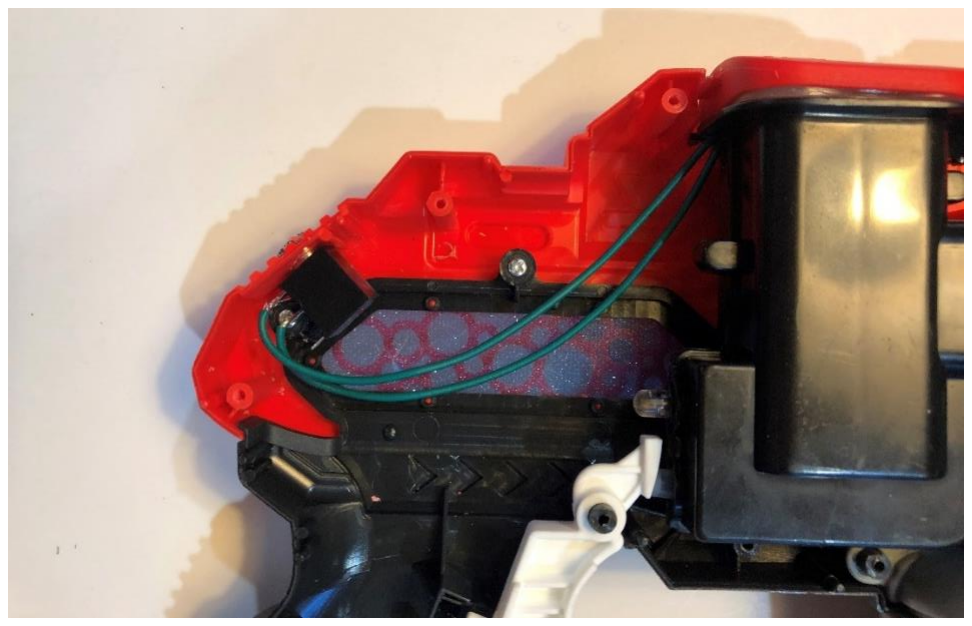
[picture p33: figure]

Files available at | https://makersmakingchange.com/project/switch-adapted-water-gun/ (https://makersmakingchange.com/?post_type=project&p=15490&preview=true) | Page 10 of 13

## Step 17

Remove the nut from the mono jack and push the mono jack through the hole. Reinstall the nut and tighten to secure.

## Step 18

Place the battery compartment and the water compartment back in the gun. If there were any screws holding these parts down, put them back in.

# ASSEMBLY GUIDE

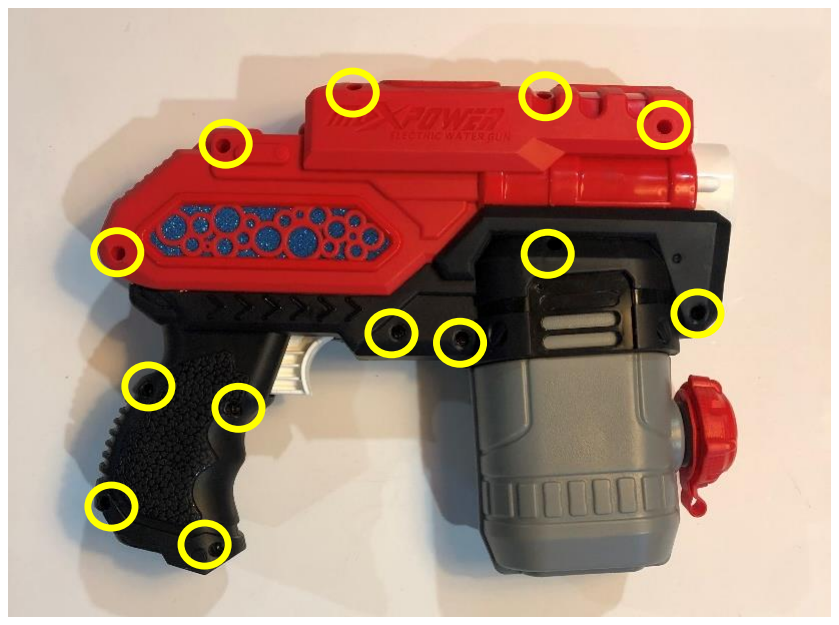
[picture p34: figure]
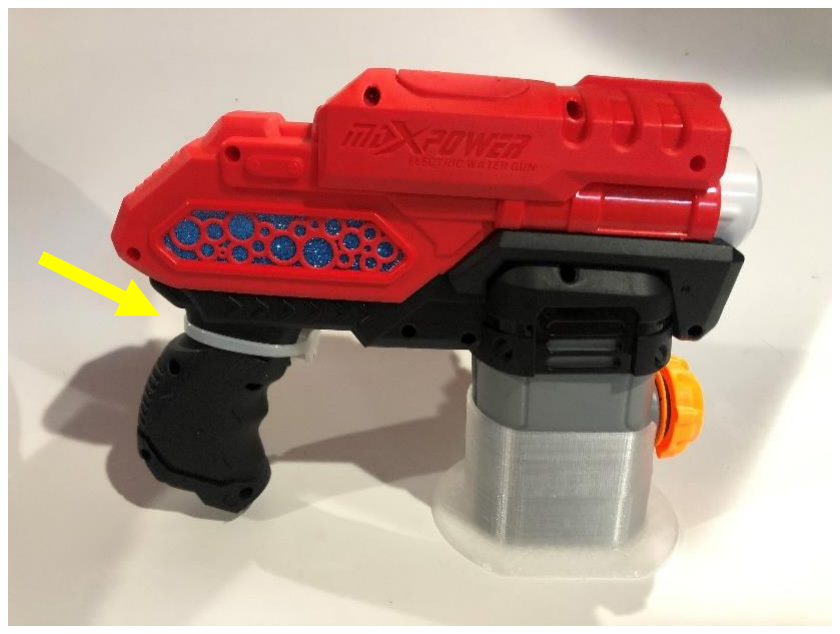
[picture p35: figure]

Files available at | https://makersmakingchange.com/project/switch-adapted-water-gun/ (https://makersmakingchange.com/?post_type=project&p=15490&preview=true) | Page 11 of 13

## Step 19

Reinsert the 13 screws to reattach the other side of the water gun.

## Step 20

Place a zip tie around the trigger on the water gun holding it in the on position. Cut any excess.

# ASSEMBLY GUIDE

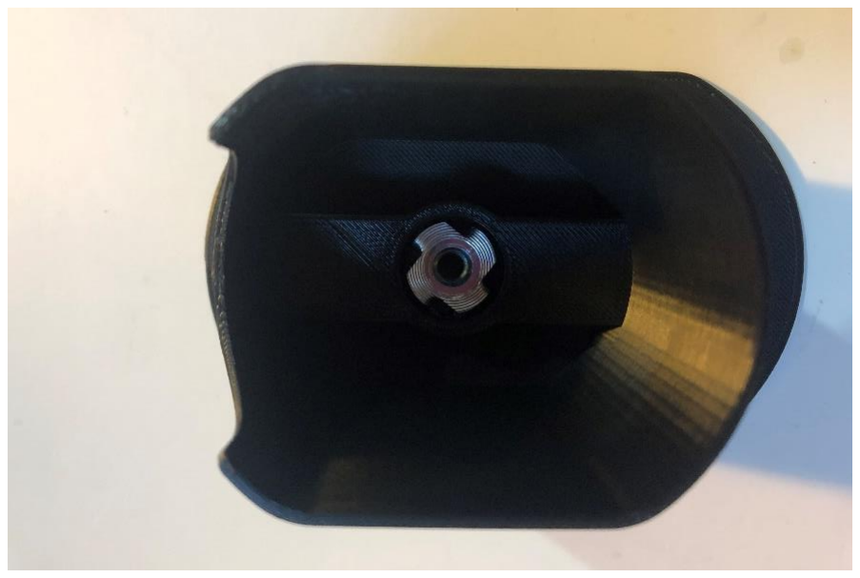
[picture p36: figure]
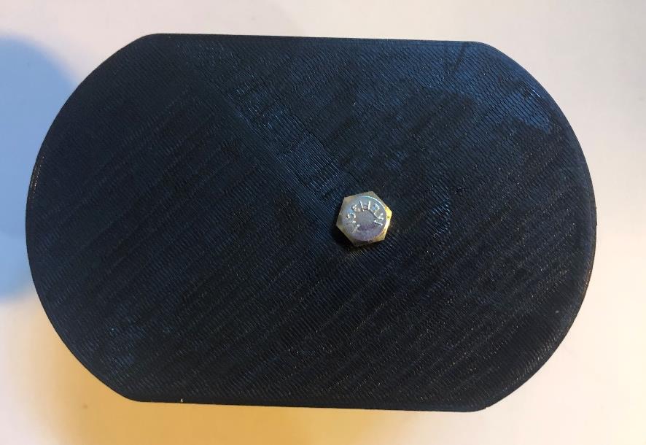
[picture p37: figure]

Files available at | https://makersmakingchange.com/project/switch-adapted-water-gun/ (https://makersmakingchange.com/?post_type=project&p=15490&preview=true) | Page 12 of 13

## Step 21

Place the tee nut teeth on the slits in the 3D printed base.

## Step 22

Thread the bolt through the nut and tighten until the tee nut is seated as far down as possible.

# ASSEMBLY GUIDE

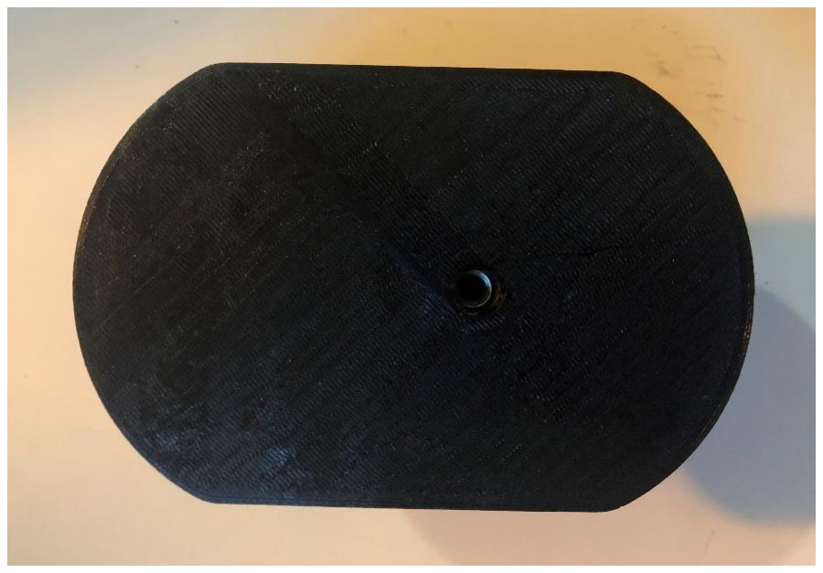
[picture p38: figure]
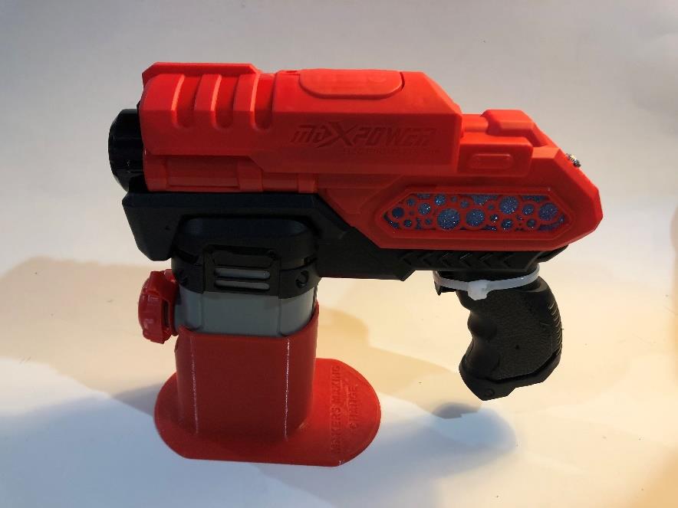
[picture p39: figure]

Files available at | https://makersmakingchange.com/project/switch-adapted-water-gun/ (https://makersmakingchange.com/?post_type=project&p=15490&preview=true) | Page 13 of 13

## Step 23

Unscrew and remove the bolt.

## Step 24

## Place the water gun in the 3D printed base

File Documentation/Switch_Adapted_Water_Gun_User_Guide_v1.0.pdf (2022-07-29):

V1.0 | JUNE 2022

## Switch Adapted Water Gun

## USER QUICK GUIDE

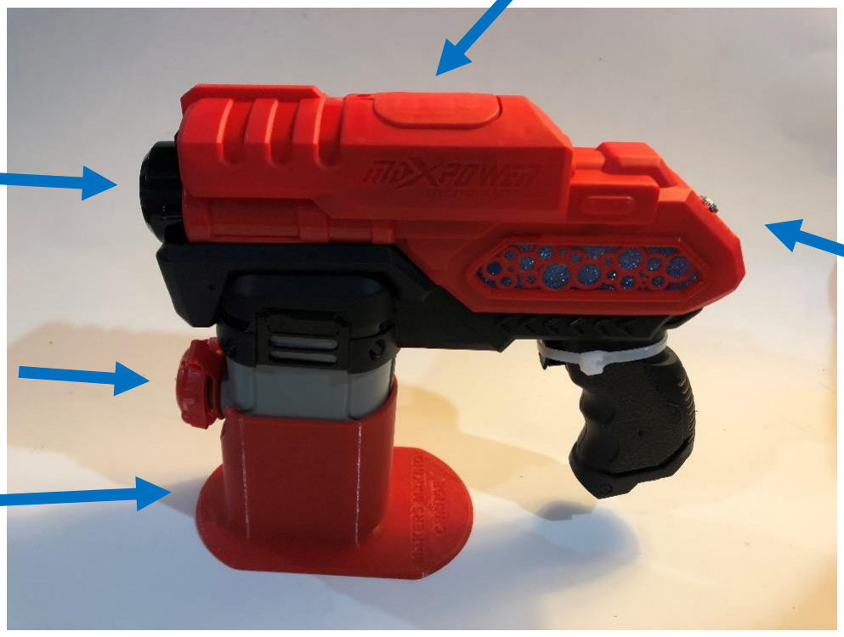
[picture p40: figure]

© 2022 by Kerilyn Kennedy – Makers Making Change This work is licensed under the CC BY SA 4.0 License: http://creativecommons.org/licenses/by-sa/4.0 Files available at https://makersmakingchange.com/project/switch-adapted-water-gun/ (https://makersmakingchange.com/?post_type=project&p=15490&preview=true)

### Introduction

This is a switch adapted water gun that is compatible with 3.5mm switches. This device may be beneficial to someone with limited hand function that is interested in using a water gun.

### Features

### Usage

The Switch Adapted Water Gun can be used by first filling it up with water. Next, plug in a 3.5mm switch into the back of the water gun. Once the switch is pressed, the water gun is activated.

### Compatibility

The Switch Adapted Water Gun should be compatible with any 3.5mm switch.

### Specifications

Length (mm) | Width (mm) | Height (mm) | Mass (g)
215 | 165 | 60 | 272
*The mass given is the mass of the empty water gun.

### Cleaning

The device can be wiped down with a damp cloth. When not in use, empty out the water compartment in the gun.

3.5mm jack

Water
compartment

Nozzle

3D Printed
Water Gun
Stand

Battery compartment

V1.0 | JUNE 2022

## Switch Adapted Water Gun

## USER QUICK GUIDE

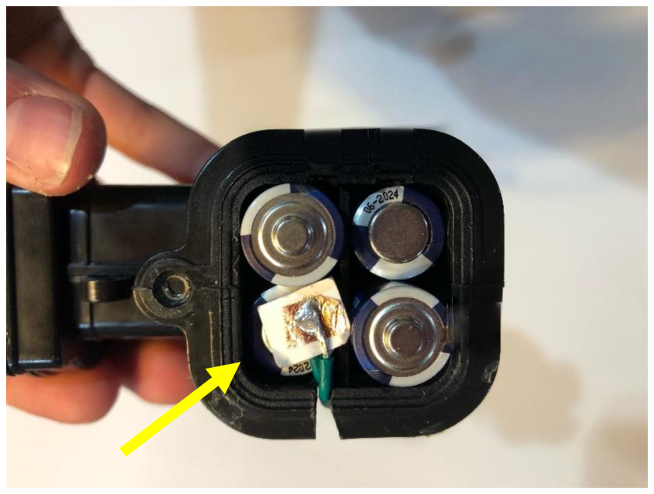
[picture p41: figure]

© 2022 by Kerilyn Kennedy – Makers Making Change This work is licensed under the CC BY SA 4.0 License: http://creativecommons.org/licenses/by-sa/4.0 Files available at https://makersmakingchange.com/project/switch-adapted-water-gun/ (https://makersmakingchange.com/?post_type=project&p=15490&preview=true)

### Changing the Batteries

The batteries can be accessed by removing the screw from the battery compartment located on the top of the water gun. The device takes 4 AA batteries. This water gun was adapted using a battery interrupter. If the batteries need to be changed in the device, the battery interrupter will have to be wedged between one of the batteries and the battery spring in the location shown below. The battery interrupter shown below is centered on the battery to ensure it is touching both the battery and the spring located on the lid. If the device is still not working once you’ve changed the batteries, this is likely caused by the battery interrupter not being placed correctly. If the water gun stays in the “on position” even though you are not holding down a switch, this means the battery interrupter is not doing its job and means it needs to be adjusted.

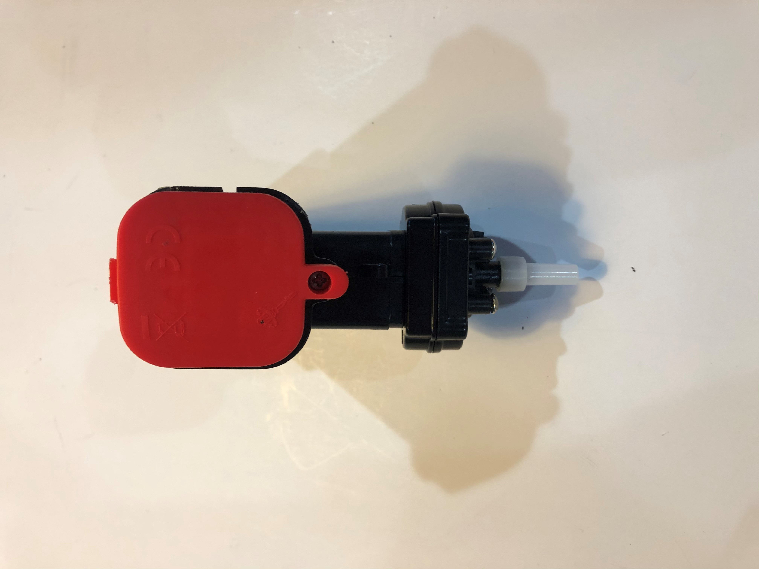
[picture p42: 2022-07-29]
Photos/Step 5.jpg

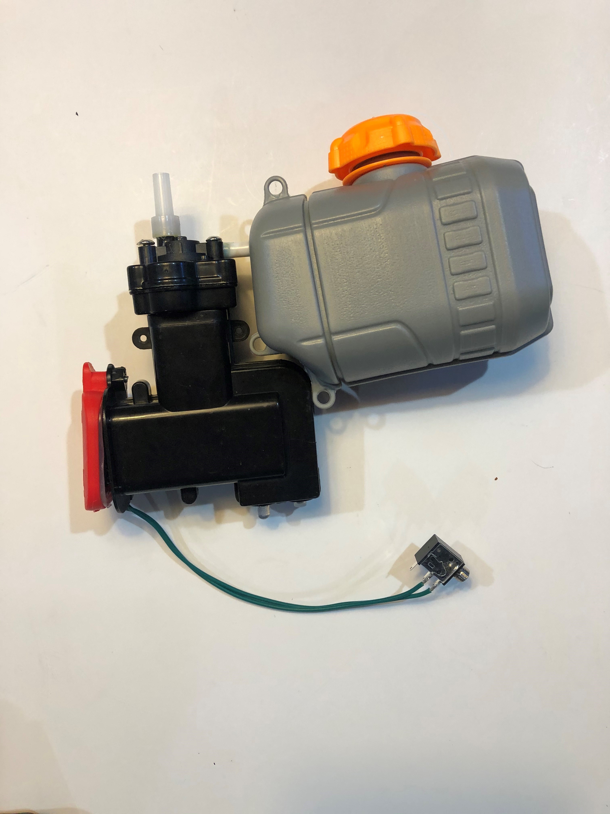
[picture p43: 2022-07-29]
Photos/Step 14.jpg

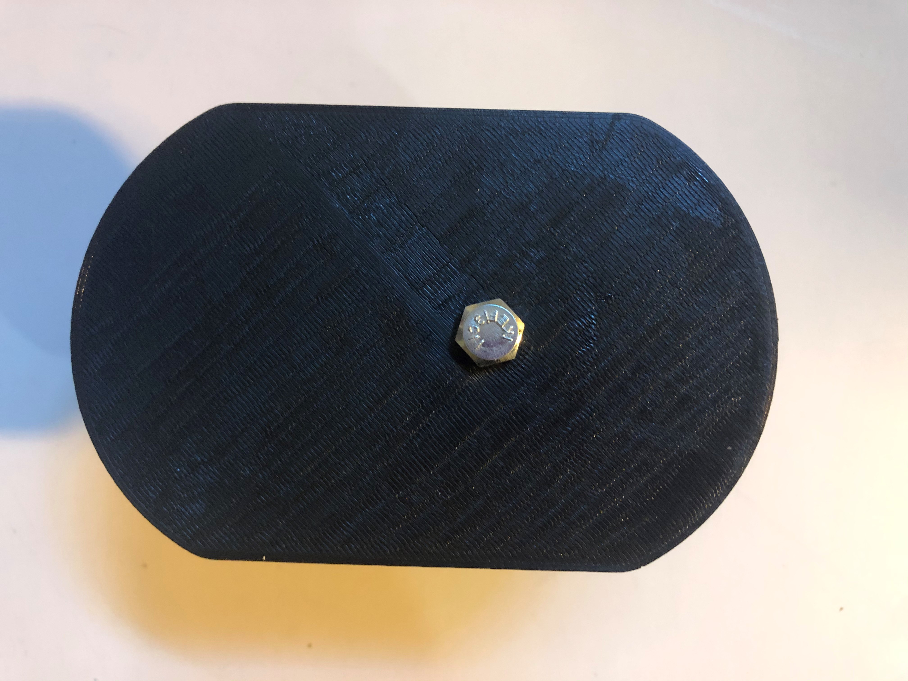
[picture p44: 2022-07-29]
Photos/Step 22.jpg

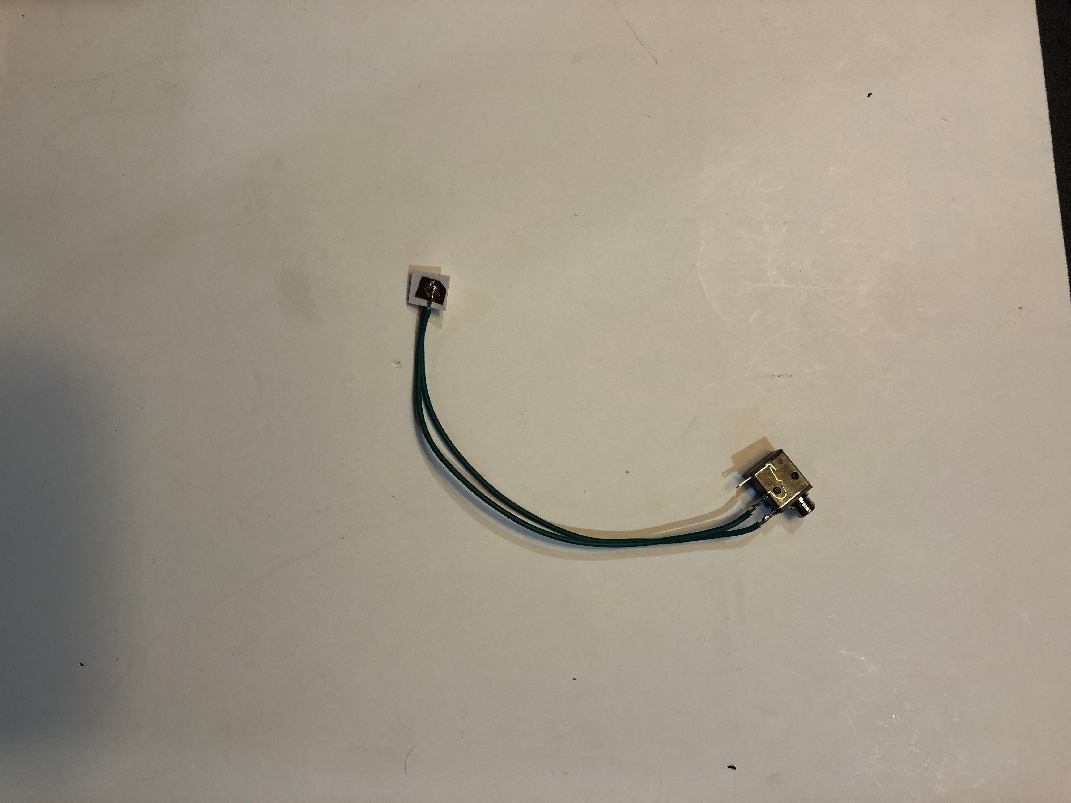
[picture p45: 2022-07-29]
Photos/Step 11.jpg

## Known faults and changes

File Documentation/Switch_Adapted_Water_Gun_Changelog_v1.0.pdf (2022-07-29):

V1.0 | JUNE 2022

# Switch Adapted Water Gun

# CHANGELOG

© 2022 by Kerilyn Kennedy – Makers Making Change. This work is licensed under the CC BY SA 4.0 License: http://creativecommons.org/licenses/by-sa/4.0 Files available at https://makersmakingchange.com/project/switch-adapted-water-gun/ (https://makersmakingchange.com/?post_type=project&p=15490&preview=true)

# Version 1.0 | Date 06/29/2022

## - Initial Version - Toy adaption designed by Kerilyn Kennedy – Makers Making Change - 3D Printed Water Gun Stand designed by Kerilyn Kennedy – Makers Making Change - Documentation by Neil Squire / Makers Making Change
